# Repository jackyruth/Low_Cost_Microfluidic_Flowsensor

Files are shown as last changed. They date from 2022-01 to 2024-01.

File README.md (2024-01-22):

# Low Cost Flowsensor
https://github.com/jackyruth/Low_Cost_Microfluidic_Flowsensor/assets/32418878/434e1281-520d-4bf3-973c-ca0241b3b97c

## Description
- Does the Job! Measures up to 80 uL/min
- Cheap! Has a BOM cost < 30CAD
- Accurate! 5% Median Accuracy < 55 uL/min, 10-18% Median Accuracy > 55uL/min
- Non-invasive! Wet components are standard 1/32' OD tygon tubing and 29G stainless steel
- Simple Interface! UART Outputs every 15 seconds

This project is also well documented:
- 'Flowsensor Product Specification.pdf': Datasheet for the flowsensor
- 'Flowsensor Requirements, Design & Verification.pdf': A document describing the requirements, design and verification of the flowsensor
- 'flowsensor_demonstration.MOV': A video showing the benchmarking process
- 'UBC_BioMEMS_Product_Video.mp4': A video describing the context of the system the flowsensor is originally designed to be a part of.

## Project Tree
```
.
├── data
├── julia
├── lsi_lab_validation
├── pcb_v1
├── README.md
├── reagent_compatibility
└── stm32
```

- 'data' contains time series temperature data measured at set flow rates
- 'julia' contains data science Pluto notebooks used to experiment with the time series temperature data and analyze benchmarking data 
- 'lsi_lab_validation' contains the benchmarking data where we pitted the low cost sensor against the Sensirion SLI-0430 FMK flowsensor
- 'pcb_v1' contains a KiCAD PCB project of the flowsensor
- 'reagent_compatibility' contains benchmarking data where we ran different reagents, some at different temperatures, through the flowsensor
- 'stm32' contains the firmware for the flowsensor

# License
The hardware design is licensed under CERN-OHL-P-2.0. All other components are licensed under Apache-2.0.

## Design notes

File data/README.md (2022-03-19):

# Data
Data comes in the following form
```
158781 26.30 0
158801 26.30 0
158821 26.31 0
158841 26.30 100
158861 26.30 100
158881 26.29 100
158901 26.29 100
158921 26.30 100
158941 26.28 100
158961 26.28 0
158981 26.28 0
```
The first column is time in milliseconds.
The second column is temperature data in Celsius
The third column is the heat pulse signal. When it is 0, the heater is off, when it is 100, the heater is on.

The data is stored in The data is stored in text files named with the corresponding flowrate.
These text files are stored in repositiories corresponding to the device used to take those measurements.

For example 'final_product/10.txt' contain time series temperature data taken by the final product at a set flow rate of 10 uL/min

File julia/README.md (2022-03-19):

# Julia
The tool we use for data analysis is julia and Pluto notebook.

As mentioned in the key documents, in order to extract the flow rate from the time series temperature data, we have to go through two steps.
1. Extract the timedelta from the time series temperature data. This process is shown in 'timedelta_detection.jl'
2. Extract the flowrate from the timedelta. This process is shown in 'flowrate_detection.jl'

We also use the same tools to analyze the benchmarking data. This process is shown in 'benchmarking.jl'

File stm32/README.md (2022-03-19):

# STM32
There are two firmware files.

The 'data_collection' firmware is used to collect timeseries temperature data.
Applying the 'flowrate_detection.jl' on that temperature data will yield the calibration constants.

The 'functional_firmware' is the main firmware which runs on the sensor and outputs the flowrate. The calibration constants are hardcoded as #define in this firmware.

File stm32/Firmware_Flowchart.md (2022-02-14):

```mermaid
flowchart TD
    HeatPulse(100 ms Heat Pulse)
    DataCollection(Collect Temperature Data)
    Sleep(Wait for 1 second)
    ArrayFull([Are there 13 data points?])
    PassThreshold([Is temperature bump significant?])
    NoFlow[[Output 0.00 uL/min]]
    LM_Algo(Solve Non-Linear Least Squares Problem)
    ConvergenceCheck([Did solution converge?])
    OOR[[Output OOR for out of range]]
    Get_Timedelta(Extract Timedelta)
    Get_Flowrate(Calculate Flow Rate)
    Flowrate_Result[[Output Flow Rate]]
	Start --> HeatPulse
	HeatPulse --> DataCollection
	DataCollection --> ArrayFull
	ArrayFull -- no -->Sleep
	Sleep --> DataCollection
	ArrayFull -- yes -->PassThreshold
	PassThreshold -- no --> NoFlow
	PassThreshold -- yes --> LM_Algo
	LM_Algo --> ConvergenceCheck
	ConvergenceCheck -- no --> OOR
	ConvergenceCheck -- yes --> Get_Timedelta
	Get_Timedelta --> Get_Flowrate
	Get_Flowrate --> Flowrate_Result

```

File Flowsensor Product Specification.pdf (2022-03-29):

# Flow Rate Sensor Specifications

# Media Isolated Microfluidic Flow Rate Sensor

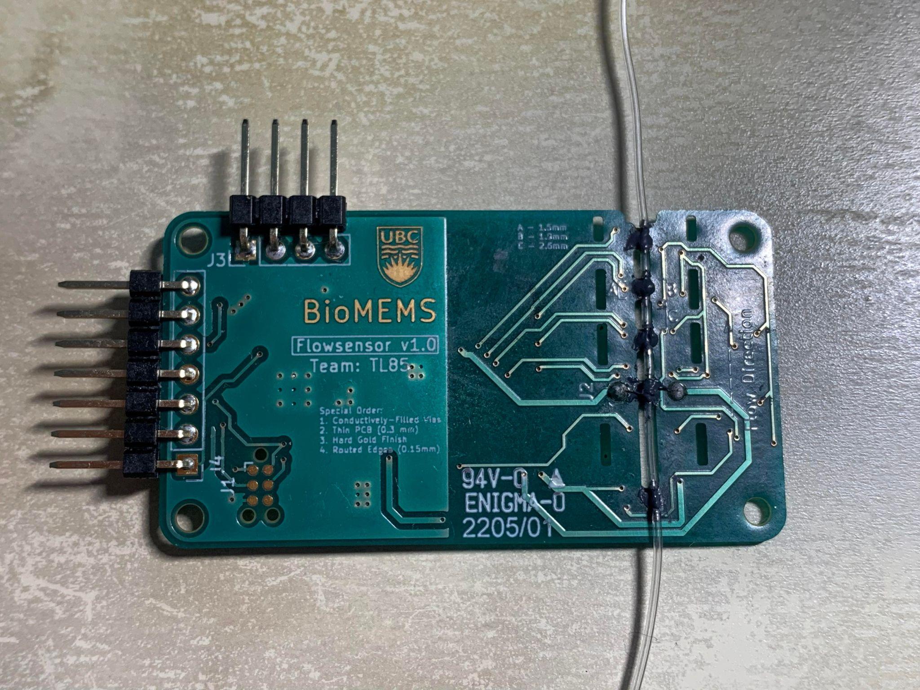
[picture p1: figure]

## - Measures up to 80 uL/min

## - Non-invasive measurement

## - Simple UART Output

## - 15 Seconds Response Time

# Electrical Characteristics

Parameter | Min | Nominal | Max | Unit
Supply Voltage | 1.8 | 3.3 | 3.6 | V
Supply Current | - | 10 | 600 (1) | mA
Response Time | 14 | 15 | 16 | s
Note 1: Drains up to 600 mA while applying power to the heater wires

# Measurement Characteristics

Parameter | Min | Nominal | Max | Unit
H2O Flow Rate Full Scale | - | - | 80 | uL/min
H2O Accuracy Below 55 uL/min | - | - | 5 | % full scale
H2O Accuracy Below 80 uL/min | - | - | 18 | % full scale
All test results taken with the following parameters
- Supply Voltage = 3.3V
- Ambient Temperature = 23 C
- Water = DDW (Distilled, Deionized Water)

# Operation & Storage Characteristics

Parameter | Min | Nominal | Max | Unit
Storage Temperature | -10 | 23 | 60 (2) | C
Operating Temperature | 10 (3) | 23 | 50 (3) | C
Storage & Operating Humidity | - | - | 95 | %RH
Maximum Reagent temperature | - | - | 30 (4) | C
Note 2: The Tygon tubing may have a lower storage temperature than this figure
Note 3: These figures are best guesses, they have not been tested
Note 4: The maximum temperature the reagent will be heated to during the measurement process

# Mechanical Characteristics

Parameter | Min | Nominal | Max | Unit
Measurement Tube Inner Diameter (5) | 0.184 | - | 0.254 | mm
H2O Pressure Drop @ full scale | - | - | 10 (6) | mbar
Total Internal Volume | - | - | 2 | uL
Max Pressure | - | - | 2000 (7) | mbar
Note 5: Measurement tube consists of alternating sections of stainless steel 29G tubes and 0.01’’ID, 1/32’’OD Tygon tubes
Note 6: Theoretical, calculated with 80uL/min as flow rate
Note 7: Experimental result where a force equivalent to 2 bars of pressure were applied to the syringe connected to the flow sensor

# Specification Charts

## Distilled, Deionized Water (DDW)

### Benchmark Result with Fluigent System (SLI-0430)

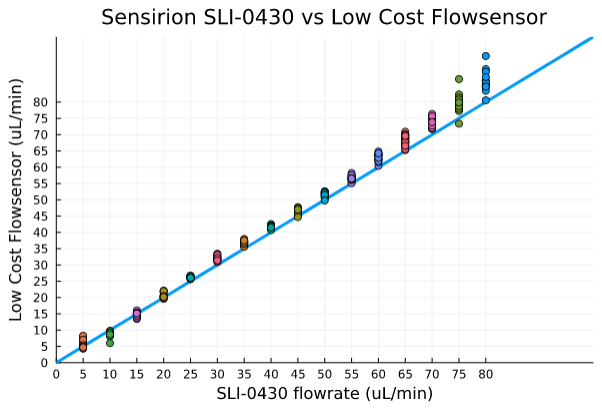
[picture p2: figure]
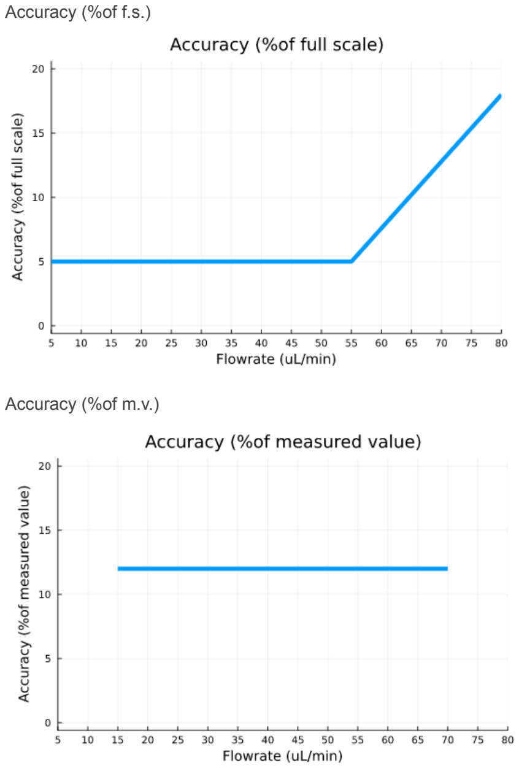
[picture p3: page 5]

### Accuracy (%of f.s.)

### Accuracy (%of m.v.)

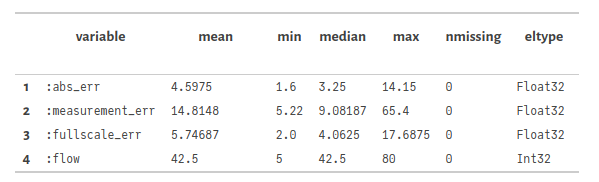
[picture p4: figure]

abs_err: uncertainty in uL/min
measurement_err: accuracy in %of measured value fullscale_err: accuracy in %of full scale
flow: Data taken between these set flow rates

## Saline Solution (10% Concentration)

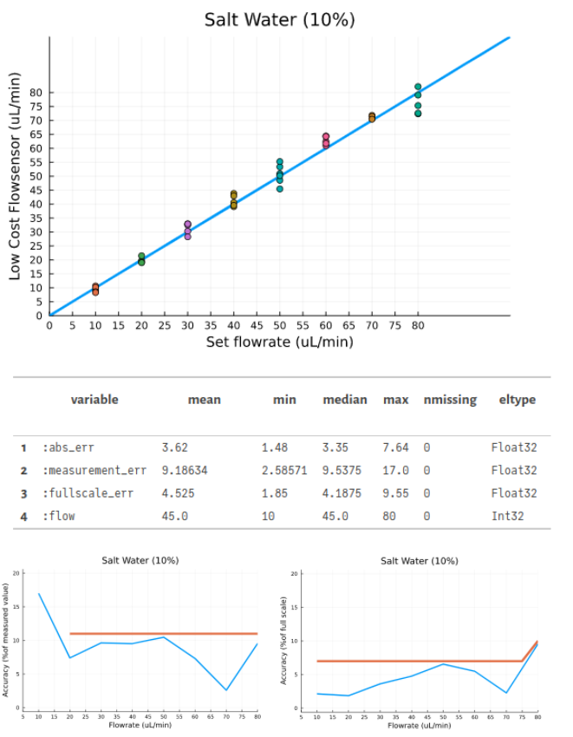
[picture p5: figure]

## 1x Phosphate Buffered Saline

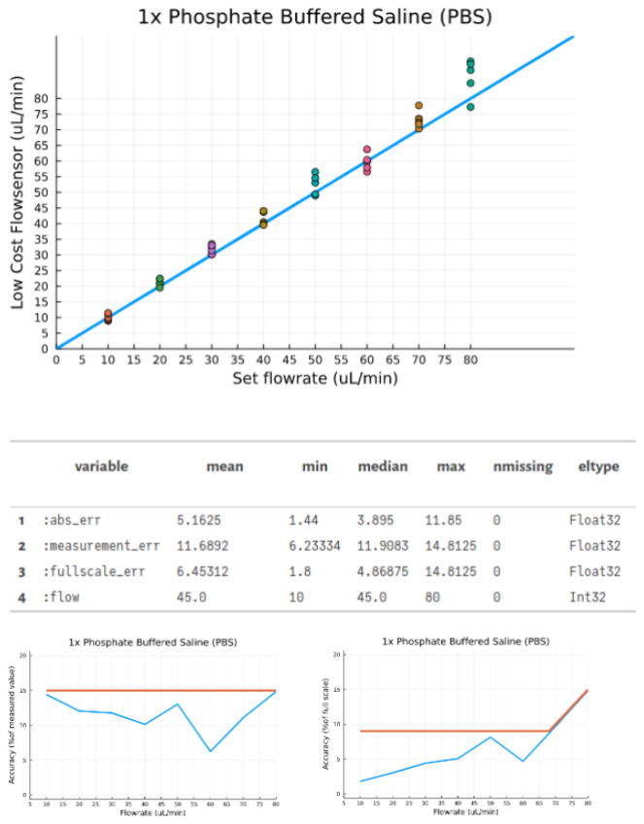
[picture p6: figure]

## 10x Phosphate Buffered Saline

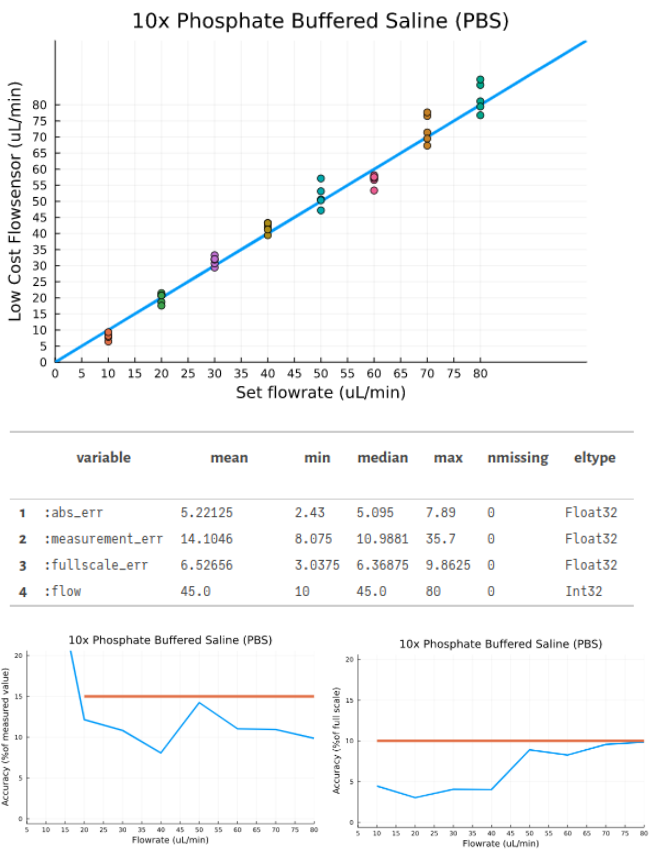
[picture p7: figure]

## Isopropyl Alcohol

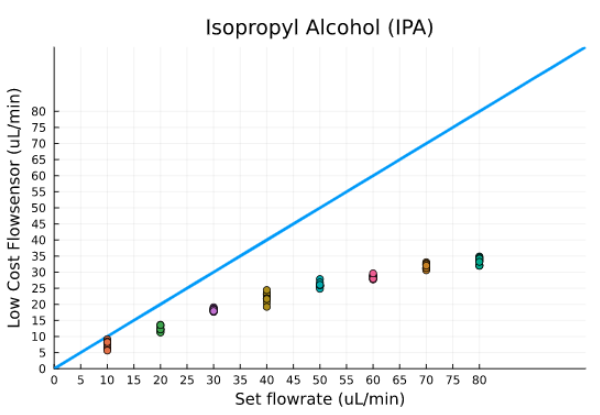
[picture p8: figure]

Sensor requires recalibration to measure IPA.

## Reagent Temperature Variation

### Water @ 10C

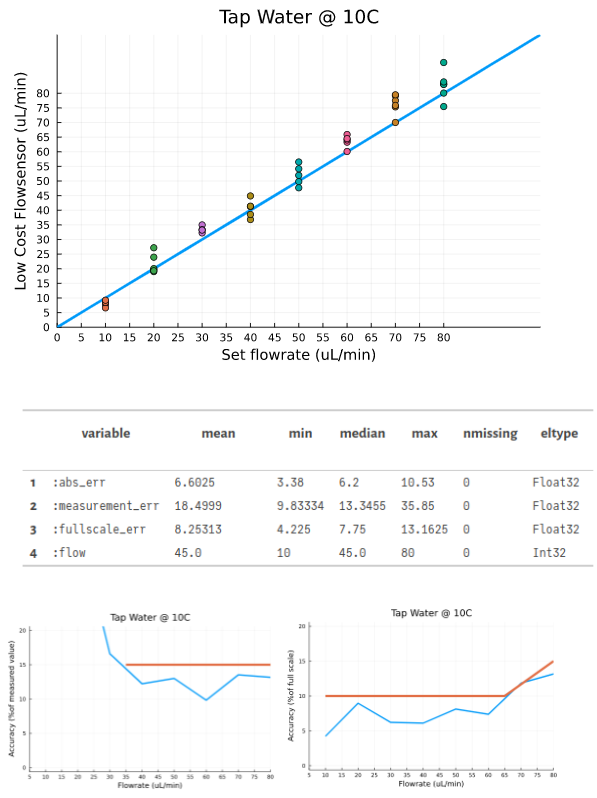
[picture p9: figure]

### Water @ 40C

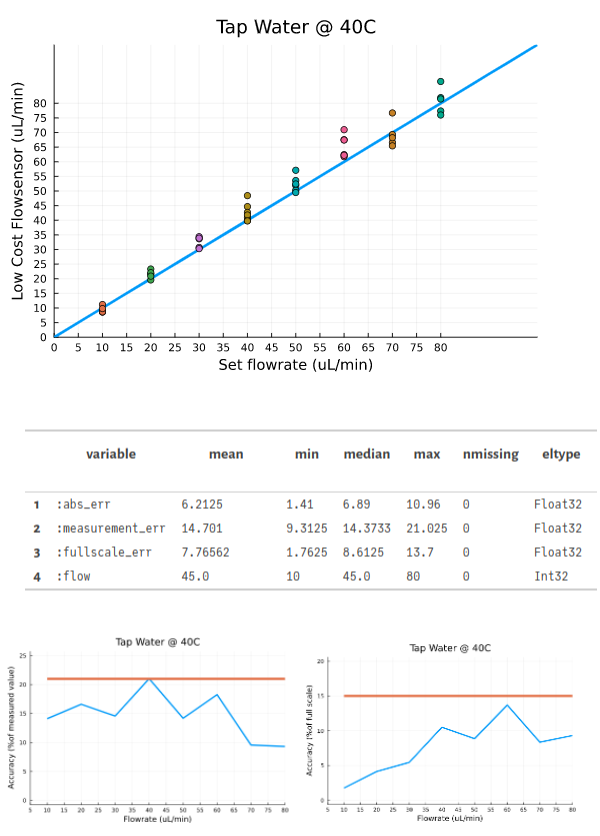
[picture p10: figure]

# Pinout

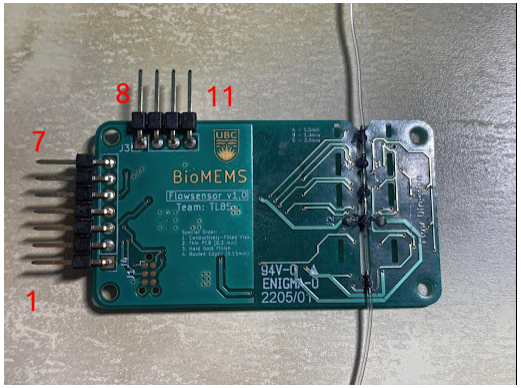
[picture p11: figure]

In the picture above, the pins are numbered 1 to 7 from bottom to top and 8 to 11 from left to right.

Pin Number | Pin Description
1, 9 | VDD
2 | SWCLK
3, 8 | GND
4 | SWDIO
5 | NRST
6 | VCP_TX
7 | VCP_RX
10,11 | Do not connect

# Calibration

Manual calibration is required. Here are the resources required for the calibration step.
1. STLINK–V3
2. Access to the github repo https://github.com/jackyruth/Low_Cost_Microfluidic_Flowsensor.git
3. A system to drive a reference flow rate

Here are the steps to calibrate the sensor
1. Connect the STLINK–V3 to the sensor, see the product specification sheet for the sensor pinout diagram
2. Program ‘stm32/data_collection’ firmware
3. Drive a constant flow rate through the sensor and store the data. Preferably, the collected data corresponds to flow rates between 5 uL/min and 80 uL/min in increments of 5 uL/min
4. Push the data through ‘julia/flowrate_detection.jl’ which outputs three calibration constants A, B and C
5. Change the calibration constants in ‘julia/functional_firmware’
Program the ‘julia/functional_firmware’ and the device should start returning proper flow rate measurements.

# Mechanical Specs

Dimensions of the sensor are 28.75x53.00 mm.

The PCB is 0.3mm thin with conductively filled vias to reduce thermal resistance.

Mounting holes are for M2 screws.

The wetted materials are stainless steel tubing cut from 29G needles and 0.01’’ ID 1/32’’ OD Tygon tubing.

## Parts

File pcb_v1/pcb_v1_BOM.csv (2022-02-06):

Id | Designator | Package | Quantity | Designation | Digikey M/N
1 | U7,U4,U3,U2,U1 | WSON-6-1EP_2x2mm_P0.65mm_EP1x1.6mm | 4 | tmp117 | 296-52215-1-ND
2 | R8,R7,R6,R5,R4,R3 | C_0603_1608Metric | 5 | 10k | 311-10KLDCT-ND
3 | C15,C13,C11,C10,C7,C6,C4,C3,C2,C1 | C_0603_1608Metric | 9 | 100nF | 311-1343-1-ND
4 | U5 | TC78H651AFNG,EL_Dual_H-Bridge | 1 | TC78H651AFNG,EL_Dual_H-Bridge | 264-TC78H651AFNGELCT-ND
5 | Y1 | ECS-.327-12.5-12R-C-TR | 1 | Crystal | XC2738CT-ND
6 | U6 | QFN-32-1EP_5x5mm_P0.5mm_EP3.45x3.45mm | 1 | STM32L432KBUx | 497-16577-ND
7 | D1 | D_SMA | 1 | D_TVS | P4SMA13ACT-ND
8 | C14,C12 | C_0603_1608Metric | 2 | 13pF | 311-3919-1-ND
9 | C9,C8 | C_0603_1608Metric | 2 | 1uF | 311-1343-1-ND
10 | C5 | C_0603_1608Metric | 1 | 10uF | 490-6405-1-ND
11 | R2,R1 | C_0603_1608Metric | 2 | 2.2k | RMCF0603FT2K20CT-ND
6 | J2 | R_Box_L8.4mm_W2.5mm_P5.08mm | 1 | Conn_01x02
7 | H4,H3,H2,H1 | MountingHole_2.2mm_M2 | 4 | MountingHole
11 | J4 | PinHeader_1x07_P2.54mm_Vertical | 1 | Conn_01x07
12 | J3 | PinHeader_1x04_P2.54mm_Vertical | 1 | Conn_01x04

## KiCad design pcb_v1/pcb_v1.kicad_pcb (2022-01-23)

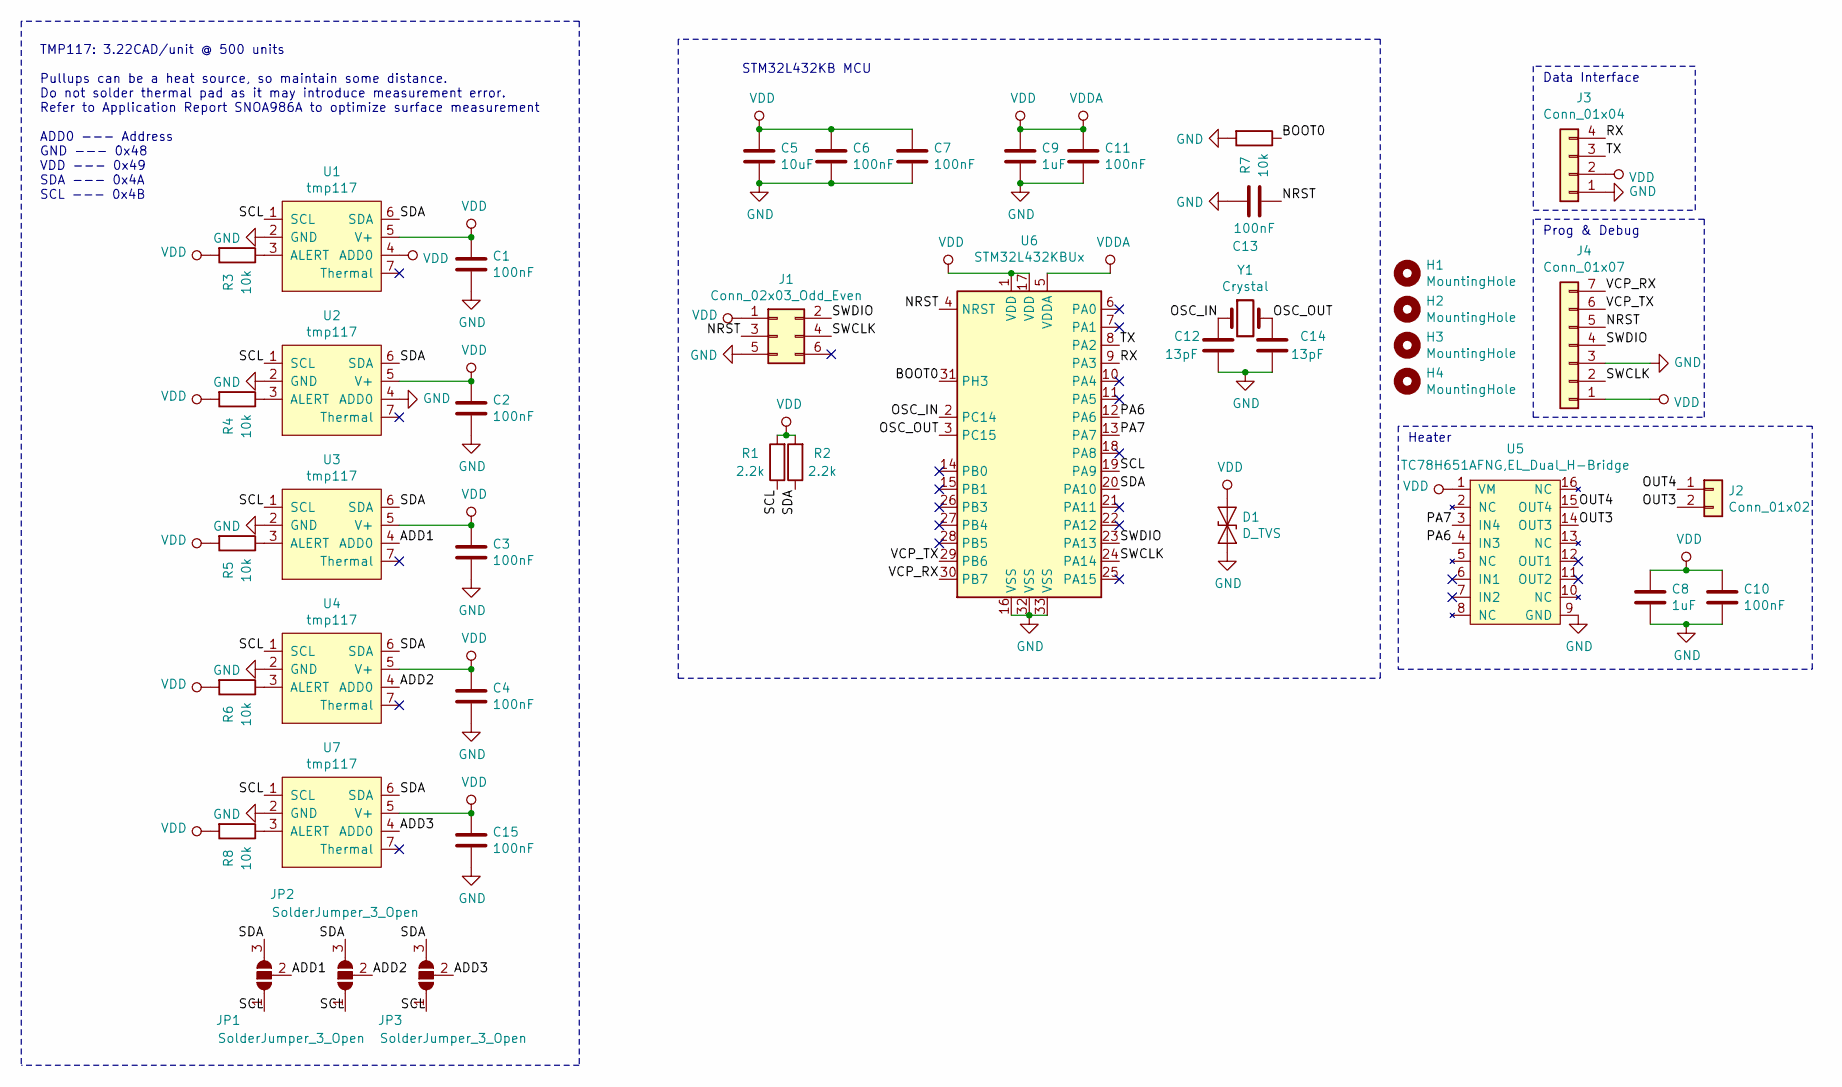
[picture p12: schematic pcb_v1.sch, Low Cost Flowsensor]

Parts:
C1, C2, C3, C4, C6, C7, C10, C11, C13, C15: 100nF; C_0603_1608Metric
C5: 10uF; C_0603_1608Metric
C8, C9: 1uF; C_0603_1608Metric
C12, C14: 13pF; C_0603_1608Metric
D1: D_TVS; D_SMA
H1, H2, H3, H4: MountingHole; MountingHole_2.2mm_M2
J1: Conn_02x03_Odd_Even; Tag-Connect_TC2030-IDC-NL_2x03_P1.27mm_Vertical
J2: Conn_01x02; R_Box_L8.4mm_W2.5mm_P5.08mm
J3: Conn_01x04; PinHeader_1x04_P2.54mm_Vertical
J4: Conn_01x07; PinHeader_1x07_P2.54mm_Vertical
JP1, JP2, JP3: SolderJumper_3_Open; SolderJumper-3_P1.3mm_Open_RoundedPad1.0x1.5mm_NumberLabels
R1, R2: 2.2k; C_0603_1608Metric
R3, R4, R5, R6, R7, R8: 10k; C_0603_1608Metric
U1, U2, U3, U4, U7: tmp117; THERMAL_ENHANCED_WSON-6-1EP_2x2mm_P0.65mm_EP1x1.6mm
U5: TC78H651AFNG,EL_Dual_H-Bridge
U6: STM32L432KBUx; QFN-32-1EP_5x5mm_P0.5mm_EP3.45x3.45mm
Y1: Crystal; ECS-.327-12.5-12R-C-TR

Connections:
/ADD1: JP1.2 (C), U3.4 (ADD0)
/ADD2: JP2.2 (C), U4.4 (ADD0)
/ADD3: JP3.2 (C), U7.4 (ADD0)
/BOOT0: R7.1, U6.31 (PH3)
/NRST: C13.2, J1.3, J4.5, U6.4 (NRST)
/OSC_IN: C12.2, U6.2 (PC14), Y1.1
/OSC_OUT: C14.2, U6.3 (PC15), Y1.2
/OUT3: J2.2, U5.14 (OUT3)
/OUT4: J2.1, U5.15 (OUT4)
/PA6: U5.4 (IN3), U6.12 (PA6)
/PA7: U5.3 (IN4), U6.13 (PA7)
/RX: J3.4, U6.9 (PA3)
/SCL: JP1.1 (A), JP2.1 (A), JP3.1 (A), R1.1, U1.1 (SCL), U2.1 (SCL), U3.1 (SCL), U4.1 (SCL), U6.19 (PA9), U7.1 (SCL)
/SDA: JP1.3 (B), JP2.3 (B), JP3.3 (B), R2.1, U1.6 (SDA), U2.6 (SDA), U3.6 (SDA), U4.6 (SDA), U6.20 (PA10), U7.6 (SDA)
/SWCLK: J1.4, J4.2, U6.24 (PA14)
/SWDIO: J1.2, J4.4, U6.23 (PA13)
/TX: J3.3, U6.8 (PA2)
/VCP_RX: J4.7, U6.30 (PB7)
/VCP_TX: J4.6, U6.29 (PB6)
GND: C1.1, C2.1, C3.1, C4.1, C5.2, C6.2, C7.2, C8.2, C9.2, C10.2, C11.2, C12.1, C13.1, C14.1, C15.1, D1.2 (A2), J1.5, J3.1, J4.3, R7.2, U1.2 (GND), U2.2 (GND), U2.4 (ADD0), U3.2 (GND), U4.2 (GND), U5.9 (GND), U6.16 (VSS), U6.32 (VSS), U6.33 (VSS), U7.2 (GND)
unnamed: R3.1, U1.3 (ALERT)
unnamed: R4.1, U2.3 (ALERT)
unnamed: R5.1, U3.3 (ALERT)
unnamed: R6.1, U4.3 (ALERT)
unnamed: R8.1, U7.3 (ALERT)
VDD: C1.2, C2.2, C3.2, C4.2, C5.1, C6.1, C7.1, C8.1, C9.1, C10.1, C11.1, C15.2, D1.1 (A1), J1.1, J3.2, J4.1, R1.2, R2.2, R3.2, R4.2, R5.2, R6.2, R8.2, U1.4 (ADD0), U1.5 (V+), U2.5 (V+), U3.5 (V+), U4.5 (V+), U5.1 (VM), U6.1 (VDD), U6.5 (VDDA), U6.17 (VDD), U7.5 (V+)

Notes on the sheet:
TMP117: 3.22CAD/unit @ 500 units Pullups can be a heat source, so maintain some distance. Do not solder thermal pad as it may introduce measurement error. Refer to Application Report SNOA986A to optimize surface measurement ADD0 --- Address GND --- 0x48 VDD --- 0x49 SDA --- 0x4A SCL --- 0x4B
STM32L432KB MCU
Prog & Debug
Data Interface
Heater

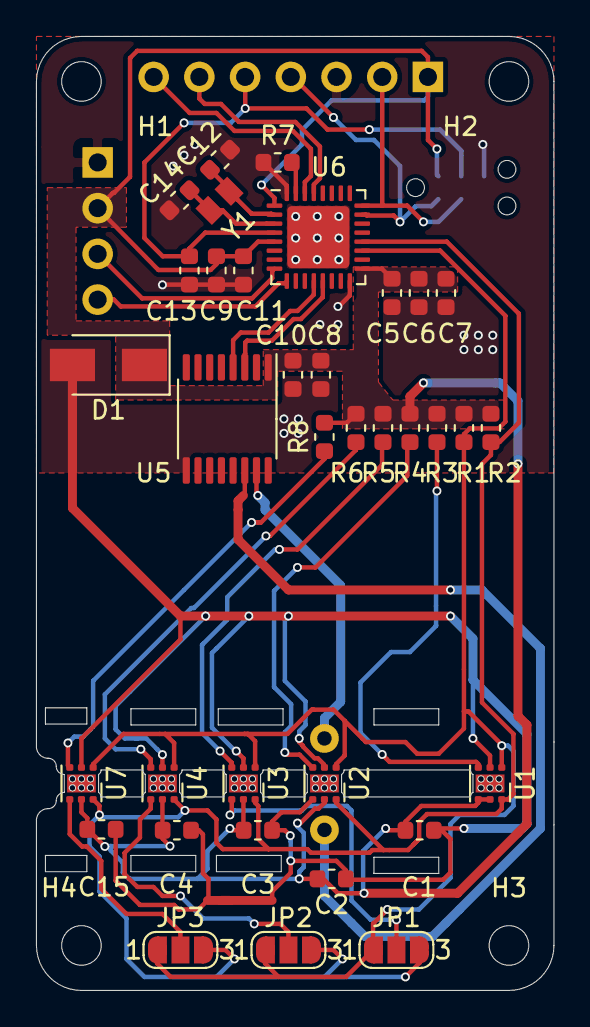
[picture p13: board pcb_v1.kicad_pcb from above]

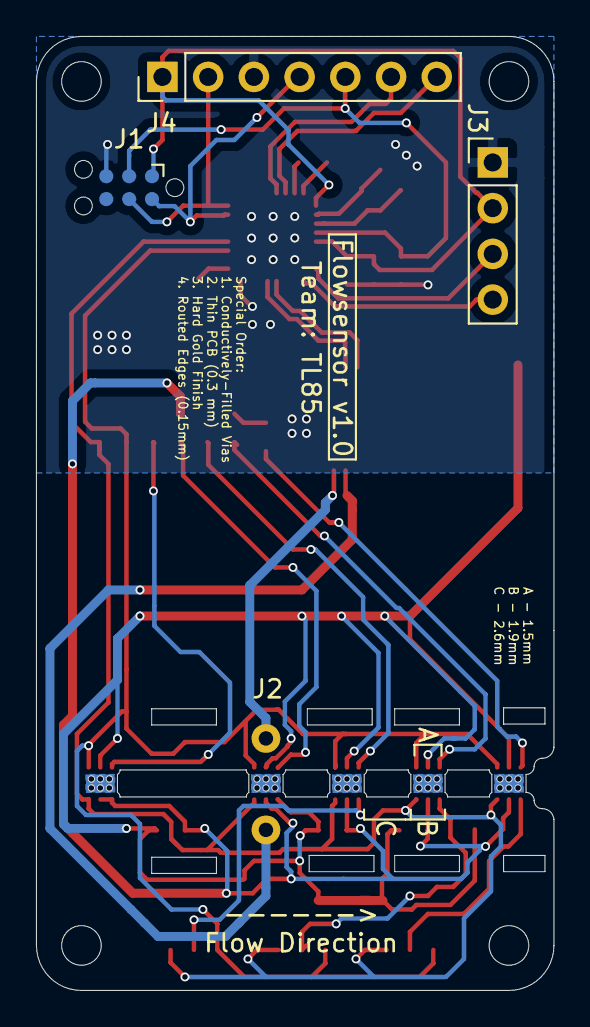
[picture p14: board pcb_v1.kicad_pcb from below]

Board: 2 copper layers, 28.8 x 53.0 mm, 43 parts (4 on the bottom side), 26 nets.

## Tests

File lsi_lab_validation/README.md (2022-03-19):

# LSI Lab Validation
Life Science Institute (LSI) Lab at the University of British Columbia (UBC) has a fluigent microfluid dispensing system.

They can dispense reagents at a regulated flow rate. The flowsensor used in this system is the Sensirion SLI-0430 FMK flowsensor. 

As described in the key documents, we connect our low cost flowsensor in series with SLI-0430. We assume that the fluigent system is regulating the flow rate perfectedly and we record the flow rate output of our low cost flowsensor and save it in text files.

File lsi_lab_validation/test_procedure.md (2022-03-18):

# Test Procedure
## Setup
1. Setup the fluigent system, use the DDW (distilled deionized water) as the test reagent
2. Connect the TL85 flowsensor in series with the client's flowsensor
3. Set the flowrate to 5 uL/min
4. Wait until TL85 measurements are steady
5. Record TL85 flowsensor output for 3 mins (12 flowrate measurements)
6. Repeat the steps above for 10, 15, 20, 25, 30, 35, 40, 45, 50, 55, 60, 65, 70, 75 and 80 uL/min

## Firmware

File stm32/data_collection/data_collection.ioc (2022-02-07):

#MicroXplorer Configuration settings - do not modify
File.Version=6
GPIO.groupedBy=Group By Peripherals
I2C1.I2C_Speed_Mode=I2C_Fast
I2C1.IPParameters=Timing,I2C_Speed_Mode
I2C1.Timing=0x2010091A
KeepUserPlacement=false
LPUART1.BaudRate=112500
LPUART1.IPParameters=WordLength,BaudRate
LPUART1.WordLength=UART_WORDLENGTH_8B
Mcu.Family=STM32L4
Mcu.IP0=I2C1
Mcu.IP1=LPUART1
Mcu.IP2=NVIC
Mcu.IP3=RCC
Mcu.IP4=SYS
Mcu.IP5=TIM1
Mcu.IP6=TIM2
Mcu.IP7=USART1
Mcu.IPNb=8
Mcu.Name=STM32L432K(B-C)Ux
Mcu.Package=UFQFPN32
Mcu.Pin0=PA0
Mcu.Pin1=PA2
Mcu.Pin10=PB7
Mcu.Pin11=VP_SYS_VS_Systick
Mcu.Pin12=VP_TIM1_VS_ClockSourceINT
Mcu.Pin13=VP_TIM2_VS_ClockSourceINT
Mcu.Pin2=PA3
Mcu.Pin3=PA6
Mcu.Pin4=PA7
Mcu.Pin5=PA9
Mcu.Pin6=PA10
Mcu.Pin7=PA13 (JTMS-SWDIO)
Mcu.Pin8=PA14 (JTCK-SWCLK)
Mcu.Pin9=PB6
Mcu.PinsNb=14
Mcu.ThirdPartyNb=0
Mcu.UserConstants=
Mcu.UserName=STM32L432KBUx
MxCube.Version=6.4.0
MxDb.Version=DB.6.0.40
NVIC.BusFault_IRQn=true\:0\:0\:false\:false\:true\:false\:false
NVIC.DebugMonitor_IRQn=true\:0\:0\:false\:false\:true\:false\:false
NVIC.ForceEnableDMAVector=true
NVIC.HardFault_IRQn=true\:0\:0\:false\:false\:true\:false\:false
NVIC.LPUART1_IRQn=true\:0\:0\:false\:true\:true\:1\:true\:true
NVIC.MemoryManagement_IRQn=true\:0\:0\:false\:false\:true\:false\:false
NVIC.NonMaskableInt_IRQn=true\:0\:0\:false\:false\:true\:false\:false
NVIC.PendSV_IRQn=true\:0\:0\:false\:false\:true\:false\:false
NVIC.PriorityGroup=NVIC_PRIORITYGROUP_4
NVIC.SVCall_IRQn=true\:0\:0\:false\:false\:true\:false\:false
NVIC.SysTick_IRQn=true\:15\:0\:false\:false\:true\:false\:true
NVIC.UsageFault_IRQn=true\:0\:0\:false\:false\:true\:false\:false
PA0.GPIOParameters=GPIO_Label
PA0.GPIO_Label=MCO
PA0.Locked=true
PA0.Signal=RCC_CK_IN
PA10.Locked=true
PA10.Mode=I2C
PA10.Signal=I2C1_SDA
PA13\ (JTMS-SWDIO).GPIOParameters=GPIO_Label
PA13\ (JTMS-SWDIO).GPIO_Label=SWDIO
PA13\ (JTMS-SWDIO).Locked=true
PA13\ (JTMS-SWDIO).Mode=Serial_Wire
PA13\ (JTMS-SWDIO).Signal=SYS_JTMS-SWDIO
PA14\ (JTCK-SWCLK).GPIOParameters=GPIO_Label
PA14\ (JTCK-SWCLK).GPIO_Label=SWCLK
PA14\ (JTCK-SWCLK).Locked=true
PA14\ (JTCK-SWCLK).Mode=Serial_Wire
PA14\ (JTCK-SWCLK).Signal=SYS_JTCK-SWCLK
PA2.Mode=Asynchronous
PA2.Signal=LPUART1_TX
PA3.Mode=Asynchronous
PA3.Signal=LPUART1_RX
PA6.GPIOParameters=PinState,GPIO_PuPd
PA6.GPIO_PuPd=GPIO_PULLDOWN
PA6.Locked=true
PA6.PinState=GPIO_PIN_RESET
PA6.Signal=GPIO_Output
PA7.GPIOParameters=PinState,GPIO_PuPd
PA7.GPIO_PuPd=GPIO_PULLDOWN
PA7.Locked=true
PA7.PinState=GPIO_PIN_RESET
PA7.Signal=GPIO_Output
PA9.Locked=true
PA9.Mode=I2C
PA9.Signal=I2C1_SCL
PB6.Locked=true
PB6.Mode=Asynchronous
PB6.Signal=USART1_TX
PB7.Locked=true
PB7.Mode=Asynchronous
PB7.Signal=USART1_RX
PinOutPanel.RotationAngle=0
ProjectManager.AskForMigrate=true
ProjectManager.BackupPrevious=false
ProjectManager.CompilerOptimize=6
ProjectManager.ComputerToolchain=false
ProjectManager.CoupleFile=false
ProjectManager.CustomerFirmwarePackage=
ProjectManager.DefaultFWLocation=true
ProjectManager.DeletePrevious=true
ProjectManager.DeviceId=STM32L432KBUx
ProjectManager.FirmwarePackage=STM32Cube FW_L4 V1.17.0
ProjectManager.FreePins=false
ProjectManager.HalAssertFull=false
ProjectManager.HeapSize=0x200
ProjectManager.KeepUserCode=true
ProjectManager.LastFirmware=false
ProjectManager.LibraryCopy=1
ProjectManager.MainLocation=Core/Src
ProjectManager.NoMain=false
ProjectManager.PreviousToolchain=STM32CubeIDE
ProjectManager.ProjectBuild=false
ProjectManager.ProjectFileName=data_collection.ioc
ProjectManager.ProjectName=data_collection
ProjectManager.RegisterCallBack=
ProjectManager.StackSize=0x400
ProjectManager.TargetToolchain=STM32CubeIDE
ProjectManager.ToolChainLocation=
ProjectManager.UnderRoot=true
ProjectManager.functionlistsort=1-MX_GPIO_Init-GPIO-false-HAL-true,2-SystemClock_Config-RCC-false-HAL-false,3-MX_LPUART1_UART_Init-LPUART1-false-HAL-true,4-MX_USART1_UART_Init-USART1-false-HAL-true,5-MX_I2C1_Init-I2C1-false-HAL-true,6-MX_TIM1_Init-TIM1-false-HAL-true,7-MX_TIM2_Init-TIM2-false-HAL-true
RCC.ADCFreq_Value=48000000
RCC.AHBFreq_Value=48000000
RCC.APB1Freq_Value=48000000
RCC.APB1TimFreq_Value=48000000
RCC.APB2Freq_Value=48000000
RCC.APB2TimFreq_Value=48000000
RCC.CK48CLockSelection=RCC_USBCLKSOURCE_MSI
RCC.CortexFreq_Value=48000000
RCC.FCLKCortexFreq_Value=48000000
RCC.FamilyName=M
RCC.HCLKFreq_Value=48000000
RCC.HSE_VALUE=8000000
RCC.HSI48_VALUE=48000000
RCC.HSI_VALUE=16000000
RCC.I2C1Freq_Value=48000000
RCC.I2C3Freq_Value=48000000
RCC.IPParameters=ADCFreq_Value,AHBFreq_Value,APB1Freq_Value,APB1TimFreq_Value,APB2Freq_Value,APB2TimFreq_Value,CK48CLockSelection,CortexFreq_Value,FCLKCortexFreq_Value,FamilyName,HCLKFreq_Value,HSE_VALUE,HSI48_VALUE,HSI_VALUE,I2C1Freq_Value,I2C3Freq_Value,LPTIM1CLockSelection,LPTIM1Freq_Value,LPTIM2Freq_Value,LPUART1Freq_Value,LSCOPinFreq_Value,LSE_VALUE,LSI_VALUE,MCO1PinFreq_Value,MSIClockRange,MSI_VALUE,PLLM,PLLPoutputFreq_Value,PLLQ,PLLQoutputFreq_Value,PLLRCLKFreq_Value,PLLSAI1N,PLLSAI1PoutputFreq_Value,PLLSAI1Q,PLLSAI1QoutputFreq_Value,PLLSAI1RoutputFreq_Value,PWRFreq_Value,RNGFreq_Value,RTCClockSelection,RTCFreq_Value,SAI1Freq_Value,SWPMI1Freq_Value,SYSCLKFreq_VALUE,USART1Freq_Value,USART2Freq_Value,USBFreq_Value,VCOInputFreq_Value,VCOOutputFreq_Value,VCOSAI1OutputFreq_Value
RCC.LPTIM1CLockSelection=RCC_LPTIM1CLKSOURCE_LSE
RCC.LPTIM1Freq_Value=32768
RCC.LPTIM2Freq_Value=48000000
RCC.LPUART1Freq_Value=48000000
RCC.LSCOPinFreq_Value=32000
RCC.LSE_VALUE=32768
RCC.LSI_VALUE=32000
RCC.MCO1PinFreq_Value=48000000
RCC.MSIClockRange=RCC_MSIRANGE_11
RCC.MSI_VALUE=48000000
RCC.PLLM=8
RCC.PLLPoutputFreq_Value=6857142.857142857
RCC.PLLQ=RCC_PLLQ_DIV4
RCC.PLLQoutputFreq_Value=12000000
RCC.PLLRCLKFreq_Value=24000000
RCC.PLLSAI1N=16
RCC.PLLSAI1PoutputFreq_Value=13714285.714285715
RCC.PLLSAI1Q=RCC_PLLQ_DIV4
RCC.PLLSAI1QoutputFreq_Value=24000000
RCC.PLLSAI1RoutputFreq_Value=48000000
RCC.PWRFreq_Value=48000000
RCC.RNGFreq_Value=48000000
RCC.RTCClockSelection=RCC_RTCCLKSOURCE_LSE
RCC.RTCFreq_Value=32768
RCC.SAI1Freq_Value=13714285.714285715
RCC.SWPMI1Freq_Value=48000000
RCC.SYSCLKFreq_VALUE=48000000
RCC.USART1Freq_Value=48000000
RCC.USART2Freq_Value=48000000
RCC.USBFreq_Value=48000000
RCC.VCOInputFreq_Value=6000000
RCC.VCOOutputFreq_Value=48000000
RCC.VCOSAI1OutputFreq_Value=96000000
USART1.BaudRate=115200
USART1.IPParameters=VirtualMode-Asynchronous,BaudRate
USART1.VirtualMode-Asynchronous=VM_ASYNC
VP_SYS_VS_Systick.Mode=SysTick
VP_SYS_VS_Systick.Signal=SYS_VS_Systick
VP_TIM1_VS_ClockSourceINT.Mode=Internal
VP_TIM1_VS_ClockSourceINT.Signal=TIM1_VS_ClockSourceINT
VP_TIM2_VS_ClockSourceINT.Mode=Internal
VP_TIM2_VS_ClockSourceINT.Signal=TIM2_VS_ClockSourceINT
board=custom
isbadioc=false

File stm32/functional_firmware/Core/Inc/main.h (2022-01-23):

/* USER CODE BEGIN Header */
/**
  ******************************************************************************
  * @file           : main.h
  * @brief          : Header for main.c file.
  *                   This file contains the common defines of the application.
  ******************************************************************************
  * @attention
  *
  * Copyright (c) 2022 STMicroelectronics.
  * All rights reserved.
  *
  * This software is licensed under terms that can be found in the LICENSE file
  * in the root directory of this software component.
  * If no LICENSE file comes with this software, it is provided AS-IS.
  *
  ******************************************************************************
  */
/* USER CODE END Header */

/* Define to prevent recursive inclusion -------------------------------------*/
#ifndef __MAIN_H
#define __MAIN_H

#ifdef __cplusplus
extern "C" {
#endif

/* Includes ------------------------------------------------------------------*/
#include "stm32l4xx_hal.h"

/* Private includes ----------------------------------------------------------*/
/* USER CODE BEGIN Includes */

/* USER CODE END Includes */

/* Exported types ------------------------------------------------------------*/
/* USER CODE BEGIN ET */

/* USER CODE END ET */

/* Exported constants --------------------------------------------------------*/
/* USER CODE BEGIN EC */

/* USER CODE END EC */

/* Exported macro ------------------------------------------------------------*/
/* USER CODE BEGIN EM */

/* USER CODE END EM */

/* Exported functions prototypes ---------------------------------------------*/
void Error_Handler(void);

/* USER CODE BEGIN EFP */

/* USER CODE END EFP */

/* Private defines -----------------------------------------------------------*/
#define MCO_Pin GPIO_PIN_0
#define MCO_GPIO_Port GPIOA
#define SWDIO_Pin GPIO_PIN_13
#define SWDIO_GPIO_Port GPIOA
#define SWCLK_Pin GPIO_PIN_14
#define SWCLK_GPIO_Port GPIOA
/* USER CODE BEGIN Private defines */

/* USER CODE END Private defines */

#ifdef __cplusplus
}
#endif

#endif /* __MAIN_H */

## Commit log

2022-01-09 Working double sensor
2022-01-16 Added single sensor code
2022-01-17 Added PCB and data
    [pcb_v1-B_Cu.gbr, pcb_v1-B_Mask.gbr, pcb_v1-B_Paste.gbr, pcb_v1-B_SilkS.gbr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]
2022-01-17 Sample model
2022-01-19 added arduino code and confirmed that glitch is caused by zephyr
2022-01-20 added cubeide code
    [pcb_v1.sch]
2022-01-20 Updated PCB w extra position
    [pcb_v1.kicad_pcb, pcb_v1.sch]
2022-01-23 updated PCB files
    [pcb_v1-B_Cu.gbr, pcb_v1-B_Mask.gbr, pcb_v1-B_Paste.gbr, pcb_v1-B_SilkS.gbr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]
2022-01-23 Added stm32cubeide code
2022-01-27 Completed data analysis and figured out how to convert temperature data to flowrate
2022-02-06 Added working levenberg implementation
    [pcb_v1_DigiBOM.csv]
2022-02-06 Successfully getting timedelta from temperature data
2022-02-07 Added data_collection firmware, currently only quickly polls from a single sensor
2022-02-08 Added pcb data
2022-02-08 Added far sensor data
2022-02-10 Finalized flowsensor project
2022-02-14 Moved BOM file to root directory
    [pcb_v1_DigiBOM.csv]
2022-03-19 cleaned repo
    [pcb_v1-B_Cu.gbr, pcb_v1-B_Mask.gbr, pcb_v1-B_Paste.gbr, pcb_v1-B_SilkS.gbr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]
2022-03-20 Added flow rate sensor product spec
2022-05-11 Added generated gerber file
    [pcb_v1-B_Cu.gbr, pcb_v1-B_Mask.gbr, pcb_v1-B_Paste.gbr, pcb_v1-B_SilkS.gbr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]
